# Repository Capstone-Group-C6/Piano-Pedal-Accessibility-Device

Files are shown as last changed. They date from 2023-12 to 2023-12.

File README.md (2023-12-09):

# Piano-Pedal-Accessibility-Device (PianoPAD)
Northeastern University 1st Place Capstone 2023 Open Source Repository for our PianoPAD system. Software designed by Roberto Chadwick, Lucas Laya Marina, and Luke Wisner. Hardware designed by Hanchen Liu, Josh Moffat, and Tristan Siu.

### General Overview
This project provides a way for people with a disability to use their piano pedals by tracking their head tilt and replicating it as pedal presses. The app is only for iOS devices, as we used Apple's Vision Library to get the necessary head tracking data. We wanted to make our work open-source so that anyone could make this device for themselves or anyone they know who would like the ability to use their piano pedals. Through the device that you plug into the piano port and the iOS application, we have created a system that can replicate pedal presses for one or three pedals. 

This idea began as a way to help Jonathan Goodwin for our engineering capstone project. Jonathan is a retired stunt performer and a current keynote speaker. Follow him at: https://www.instagram.com/jonathangoodwinofficial/?hl=en

Jonathan loves to play the piano, but he is unable to use the pedals because he was paralyzed from the waist down in an accident. We set out to create a device that would allow him to once again get full use from his piano. Through our initial meetings with Jonathan, we were able to discern the simplest, most intuitive way to make that possible: using the tilt of his head. The solutions that exist today all require the user to bite down on or blow into a device, but that would prevent Jonathan from being able to sing when he plays. The head tilt became the perfect solution because it fixed this issue while remaining intuitive to the user.

## Hardware
### Hardware Overview
One half of the PianoPAD system is the device that plugs into the back of the piano and replicates the pedal press signal. Anyone who wants to use this design in the future will need a chip capable of sending and recieving data over bluetooth (we used an ESP32 as a relatively inexpensive option so our schematics match that). In addition, they will need a way to power the device through micro-USB and connect the device to their piano pedal port using 1/4-inch jacks.

### Hardware Replication
The necessary KiCad files (schematic and PCB layout) have been added to allow anyone to replicate our board for their own personal use. The following images display the schematic design as well as the PCB layout of the components and traces involved in integrating all the parts of the board. 

<p align="center">
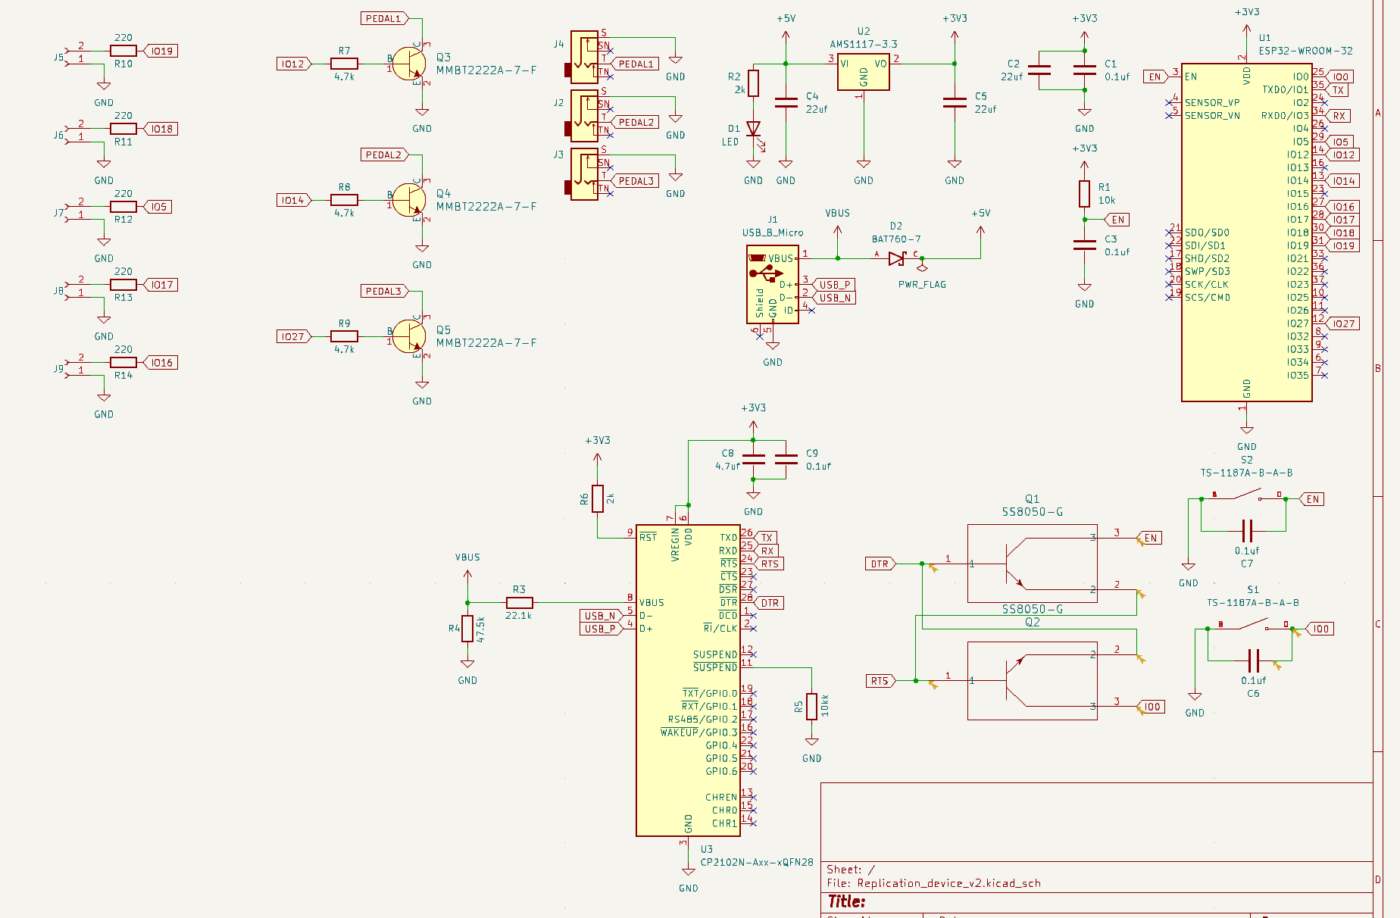
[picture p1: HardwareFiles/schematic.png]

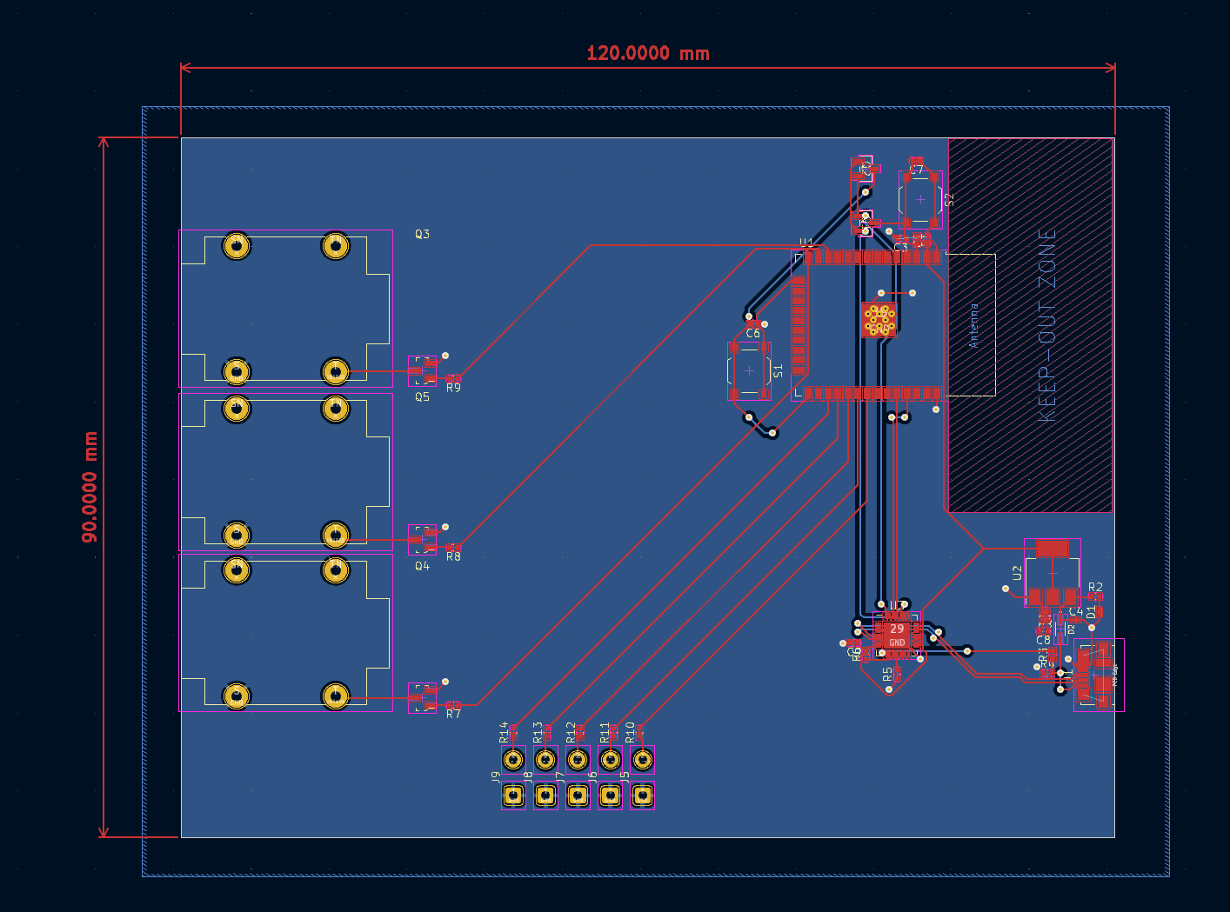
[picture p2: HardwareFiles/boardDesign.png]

</p>

In terms of the manufacturing and assembly process, orders can be made through various PCB manufacturers (we used JLCPCB.com) and provide them with our PCB/schematic files to make an order. Below is the part list with links to sites to purchase each component. (NOTE: You can also import the provided files into the KiCad project manager to view/make any changes to the project) In terms of assembly, be sure to solder on the components that are not already assembled onto the board from the manufacturer (i.e. 1/4" sockets...).

Parts List:
- 1/4" Socket: https://www.amazon.com/dp/B07MR2TT3Q?psc=1&smid=A34H4GNHCXU7L2&ref_=chk_typ_imgToDp
- LEDs: (https://www.amazon.com/eBoot-Pieces-Emitting-Diodes-Assorted/dp/B06XPV4CSH/ref=sr_1_8?crid=1UQGUEZ7QY5KU&keywords=leds&qid=1701737252&sprefix=leds%2Caps%2C88&sr=8-8&th=1)
- ESP32 Chip: [https://www.amazon.com/Development-Microcontroller-Integrated-Antenna-Amplifiers/dp/B09GK74F7N/ref=sr_1_1_sspa?crid=18ESI34J05HVB&keywords=esp32&qid=1701737319&sprefix=esp32%2Caps%2C82&sr=8-1-spons&sp_csd=d2lkZ2V0TmFtZT1zcF9hdGY&psc=1](https://www.amazon.com/Espressif-ESP32-S3-WROOM-1U-ESP32-S3-WROOM-1U-N8R8-Module/dp/B0B8NWF4F5/ref=sr_1_3?crid=3B4YTQOZYAYG1&keywords=esp32%2Bwroom%2B1u&qid=1701827727&sprefix=esp32%2Bwroom%2B1u%2Caps%2C95&sr=8-3&th=1)

### Three Pedal Proprietary Cable
Using three pedals with the device is a little more complicated because of how digital pianos are made. Any piano that can have a three-pedal attachment makes that connection through a proprietary cable instead of a standard 1/4-inch jack, so it was impossible to design a one-size-fits-all solution. Any users who want to use this functionality will have to create their own cable that ends in three 1/4-inch jacks to connect to the device. That way the other end of that cable can be the proper connection port that will work for their specific piano.

## Software
### Software Overview
The other half of the PianoPAD system is the iOS application that detects the head tilt and sends the signal over Bluetooth to the device. The app can be pushed to a TestFlight app for sharing with others, or the user can build directly to their phone through XCode. The app contains settings for selecting one or three pedals, changing the tilt direction, adjusting the threshold angle that triggers the tilt, toggling hold, and toggling inverse. The app has an additional page to give the user some directions on how to connect to the device through Bluetooth, and the best way to orient the phone when beginning a session. When the session view is started, it takes all of the saved data from settings, tracks the user's face, and begins sending data to the device to replicate the signal of the pedal press.

### Firmware Overview
The firmware that needs to be uploaded to the ESP32 chip also exists within this repository. It activates the necessary GPIO pins when it receives the packet from the application and it also contains the code necessary to establish the Bluetooth connection. The firmware then reads the sent byte to determine if any of the pedals are held down and which GPIO pins are activated if so.

### Bluetooth Connection
As stated above, the device establishes a connection when it is powered on, and the app with the corresponding UUID will be what it connects to. When the session is started in the app, it begins sending bytes where the last 3 bits trigger which pedals are currently being held down. 

### Head Tracking
The head tracking uses Apple's Vision Library to isolate features on the face and then return facial position data. This data includes the roll (tilting head side to side) and the pitch (tilting head up and down) in radians which allow us to determine the angle from the center position. The session tracks if the input radian threshold has been passed using this data, and that determines what data we send to the device to press the correct pedal. There is also a debounce implemented to prevent data flip-flopping when the user keeps their head right on the threshold. Additionally, the polling rate of the data is based on how new the iOS device is. The newer the device the smoother it will function, and we don't recommend running this system on anything older than an iPhone X.

### Navigating Settings
The settings page in the top right corner of the app allows the user to adjust what feels best to them when the session is running. There are two tabs for one pedal and three-pedal, which determines if the session will try to detect one or three directions. In the one pedal tab, the user has the ability to determine which way they want to tilt their head to pass the threshold, either left, right, both, or down. In addition, there are options to toggle inverse which presses the pedal unless the threshold is crossed, and toggle hold which keeps the state of the pedal when the threshold is crossed. There is a slider to adjust the angle with an example threshold bar beneath so that the user can test that angle and see what feels best for them. It was important to us to give the user as much freedom as possible to configure their sessions however they wanted to be natural for them.

<p align="center">
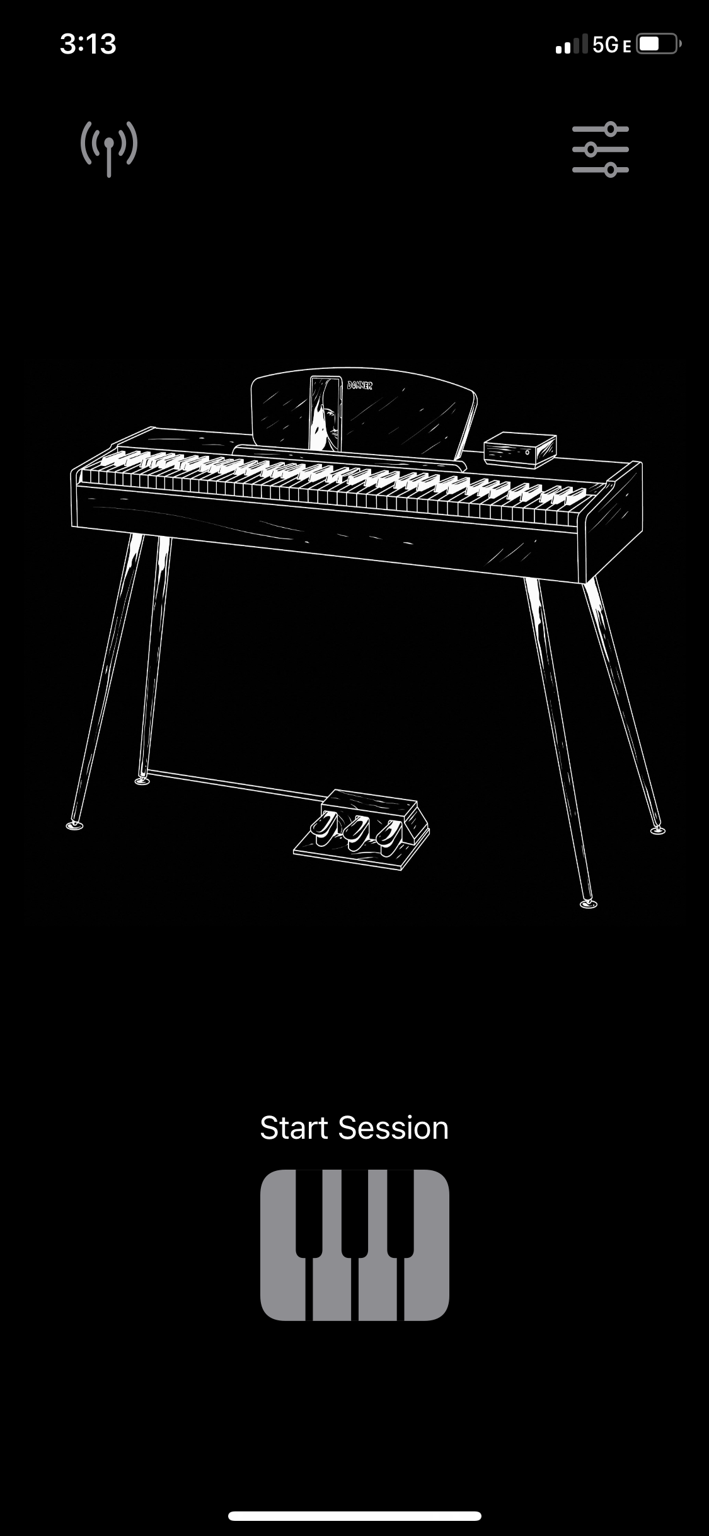
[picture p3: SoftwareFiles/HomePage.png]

</p>

<p align="center">
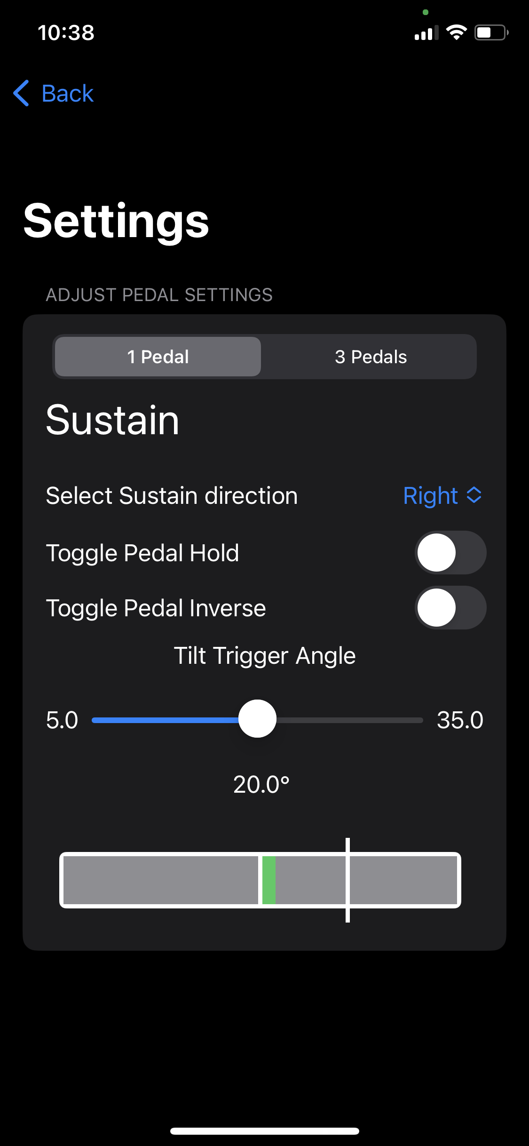
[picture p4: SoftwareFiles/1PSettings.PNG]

</p>

In the three-pedal system, the same options are available, except for the ability to hold and change directions for each pedal. The sustain and sostenuto pedals can have their directions switched to change which one is left and right, but the soft pedal is locked as tilting downward. This is because when playing the piano, the soft pedal is the only other pedal that can be used in tandem with the other two. Given that you can't tilt your head both left and right at the same time, but you can tilt down and right, we decided to keep the soft pedal as only down. Each of these three pedals has the ability to be active or inactive, so if a song doesn't require a specific pedal, you can turn it off to avoid triggering it by accident. These pedals also all have angle adjustment sliders and threshold bars to give the user a visual of what angles would work best for them.

<p align="center">
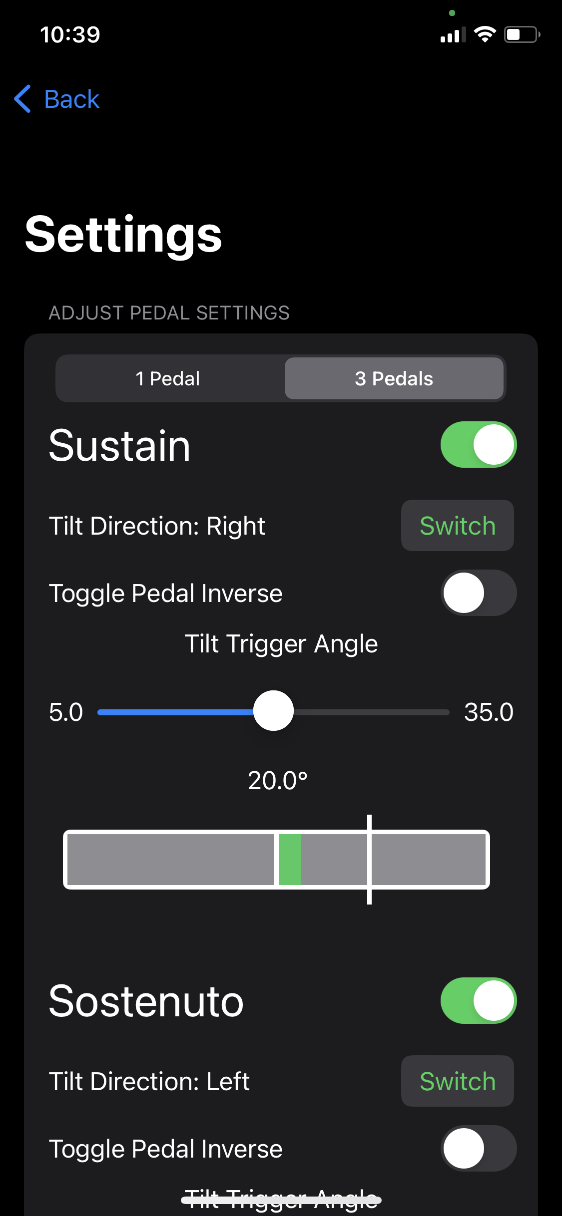
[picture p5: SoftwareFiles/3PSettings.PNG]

</p>

When the session begins, the saved settings variables are processed between specified cases that run the head-tracking logic. There is a case to handle every possible combination of toggles and angle values in both the one and three-pedal systems. The user can then see these settings in action through the indicator bars in the session view. There are the same threshold bars to show how far the user's head is tilting, and at the bottom, there are indicator bars to show which pedals are activated and sending a signal to the device.

<p align="center">
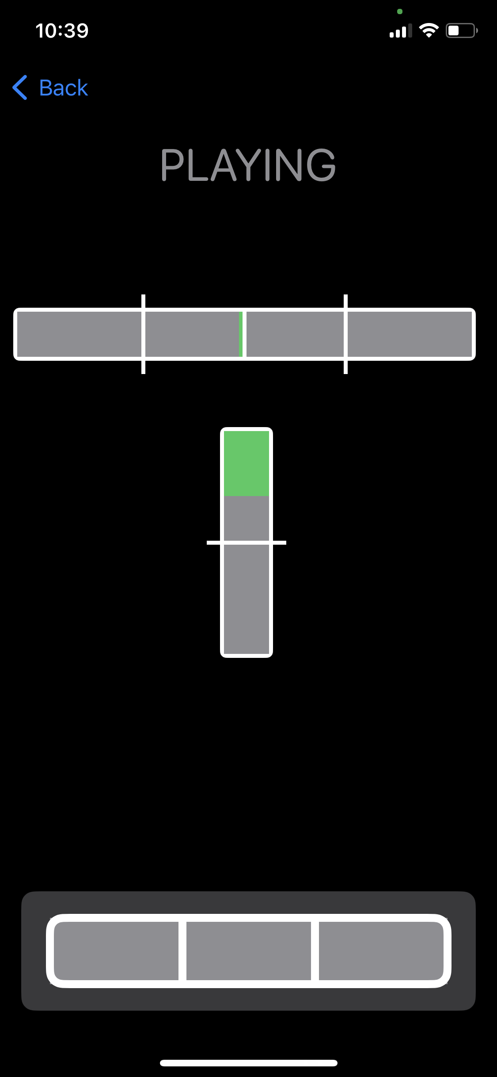
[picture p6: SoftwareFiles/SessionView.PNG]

</p>

### Software Replication
To replicate the software, the user will need to flash the firmware onto the chip they have started using. From there, the app can be run through XCode with no additional changes and be built into an iPhone for testing. Additionally, if the user wants to share the app with others, they can get an Apple Developer License and push the app to TestFlight where it can be downloaded on any iOS device. The backend functions that deal with Bluetooth connection and face tracking can be found in the model, and all of the frontend app pages can be found in the view. 

## Additional Implementations 
Another reason that we wanted to make this code publicly available is that it has so many other applications to help anyone with disabilities. We designed the app with a piano in mind, but the code can be repurposed to work with another instrument such as a guitar or drumset. Further beyond this, the head tracking functions could be expanded upon to communicate with non-instrument devices like a wheelchair. We hope that this code can help any who uses it!

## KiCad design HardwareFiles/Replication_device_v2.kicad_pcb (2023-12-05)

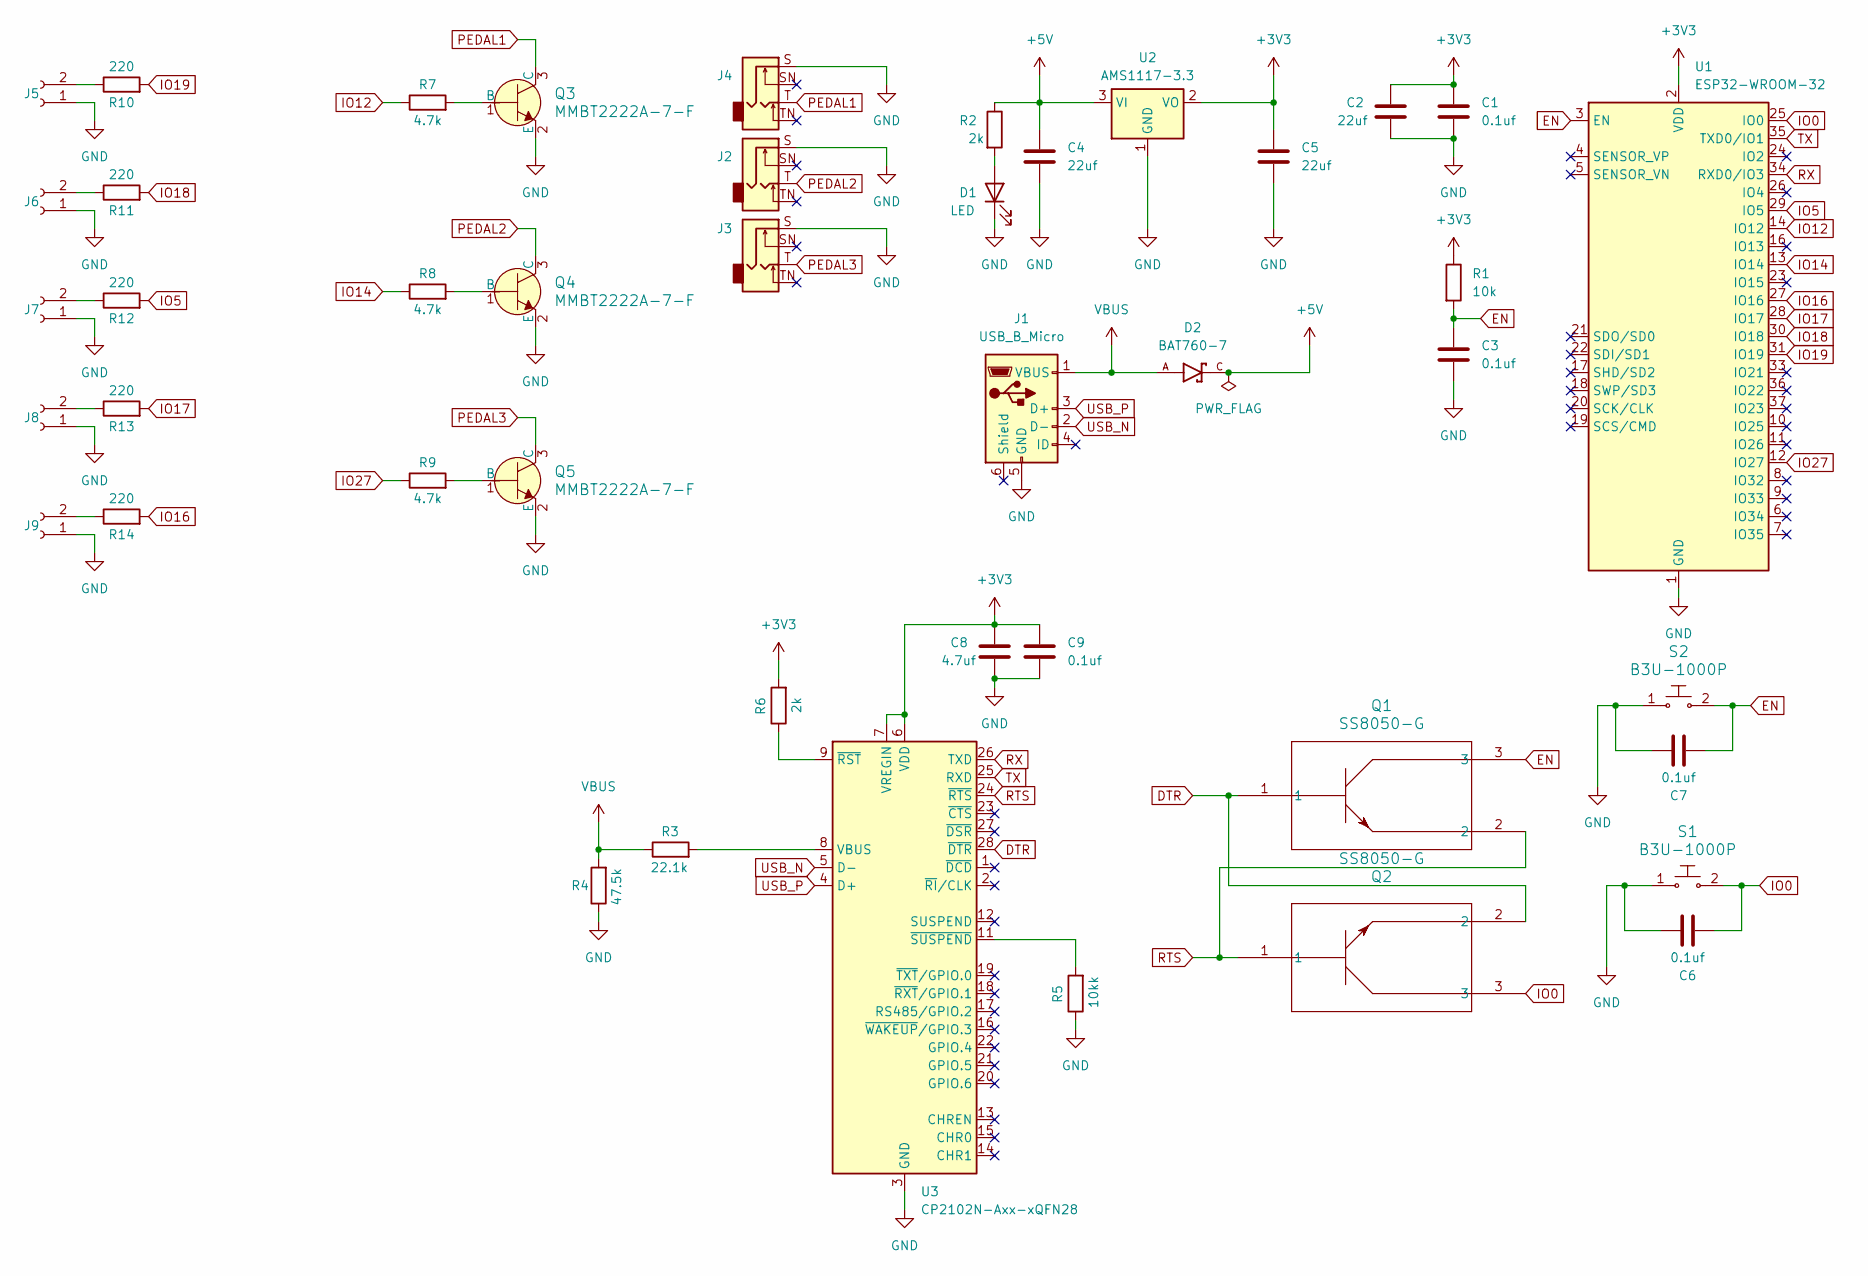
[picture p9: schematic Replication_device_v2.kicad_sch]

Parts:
C1, C3, C6, C7, C9: 0.1uf; C_0402_1005Metric
C2, C4, C5: 22uf; C_0603_1608Metric
C8: 4.7uf; C_0402_1005Metric
D1: LED; LED_0603_1608Metric
D2: BAT760-7; SOD2513X120N; PARTREV 9-2
J1: USB_B_Micro; USB_Micro-B_Molex_47346-0001
J2, J3, J4: AudioJack2_Switch; Jack_6.35mm_Neutrik_NMJ4HCD2_Horizontal
J5, J6, J7, J8, J9: Conn_01x02_Socket; SolderWire-0.5sqmm_1x02_P4.6mm_D0.9mm_OD2.1mm
Q1, Q2: SS8050-G; TRAN_SS8050-G_CIP
Q3, Q4, Q5: MMBT2222A-7-F; SOT-23-3; MPN MMBT2222A-7-F; Digi-Key_PN MMBT2222A-FDICT-ND
R1: 10k; R_0402_1005Metric
R2, R6: 2k; R_0402_1005Metric
R3: 22.1k; R_0402_1005Metric
R4: 47.5k; R_0402_1005Metric
R5: 10kk; R_0402_1005Metric
R7, R8, R9: 4.7k; R_0402_1005Metric
R10, R11, R12, R13, R14: 220; R_0402_1005Metric
S1, S2: B3U-1000P; SW_Push_1P1T_XKB_TS-1187A; MPN B3U-1000P; Digi-Key_PN SW1020CT-ND
U1: ESP32-WROOM-32
U2: AMS1117-3.3; SOT-223-3_TabPin2
U3: CP2102N-Axx-xQFN28; QFN-28-1EP_5x5mm_P0.5mm_EP3.35x3.35mm

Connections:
+3V3: C1.1, C2.1, C5.1, C8.1, C9.1, R1.1, R6.2, U1.2 (VDD), U2.2 (VO), U3.6 (VDD), U3.7 (VREGIN)
+5V: C4.1, D2.C, R2.1, U2.3 (VI)
DTR: Q1.1, Q2.2, U3.28 (~DTR)
EN: C3.1, C7.2, Q1.3, R1.2, S2.2, U1.3 (EN)
GND: C1.2, C2.2, C3.2, C4.2, C5.2, C6.1, C7.1, C8.2, C9.2, D1.1 (K), J1.5 (GND), J2.S, J3.S, J4.S, J5.1, J6.1, J7.1, J8.1, J9.1, Q3.2 (E), Q4.2 (E), Q5.2 (E), R4.1, R5.1, S1.1, S2.1, U1.1 (GND), U1.15 (GND), U1.38 (GND), U1.39 (GND), U2.1 (GND), U3.3 (GND), U3.29 (GND)
IO0: C6.2, Q2.3, S1.2, U1.25 (IO0)
IO5: R12.2, U1.29 (IO5)
IO12: R7.1, U1.14 (IO12)
IO14: R8.1, U1.13 (IO14)
IO16: R14.2, U1.27 (IO16)
IO17: R13.2, U1.28 (IO17)
IO18: R11.2, U1.30 (IO18)
IO19: R10.2, U1.31 (IO19)
IO27: R9.1, U1.12 (IO27)
unnamed: D1.2 (A), R2.2
unnamed: J5.2, R10.1
unnamed: J6.2, R11.1
unnamed: J7.2, R12.1
unnamed: J8.2, R13.1
unnamed: J9.2, R14.1
unnamed: Q3.1 (B), R7.2
unnamed: Q4.1 (B), R8.2
unnamed: Q5.1 (B), R9.2
unnamed: R3.2, U3.8 (VBUS)
unnamed: R6.1, U3.9 (~RST)
unnamed: R5.2, U3.11 (~SUSPEND)
PEDAL1: J4.T, Q3.3 (C)
PEDAL2: J2.T, Q4.3 (C)
PEDAL3: J3.T, Q5.3 (C)
RTS: Q1.2, Q2.1, U3.24 (~RTS)
RX: U1.34 (RXD0/IO3), U3.26 (TXD)
TX: U1.35 (TXD0/IO1), U3.25 (RXD)
USB_N: J1.2 (D-), U3.5 (D-)
USB_P: J1.3 (D+), U3.4 (D+)
VBUS: D2.A, J1.1 (VBUS), R3.1, R4.2

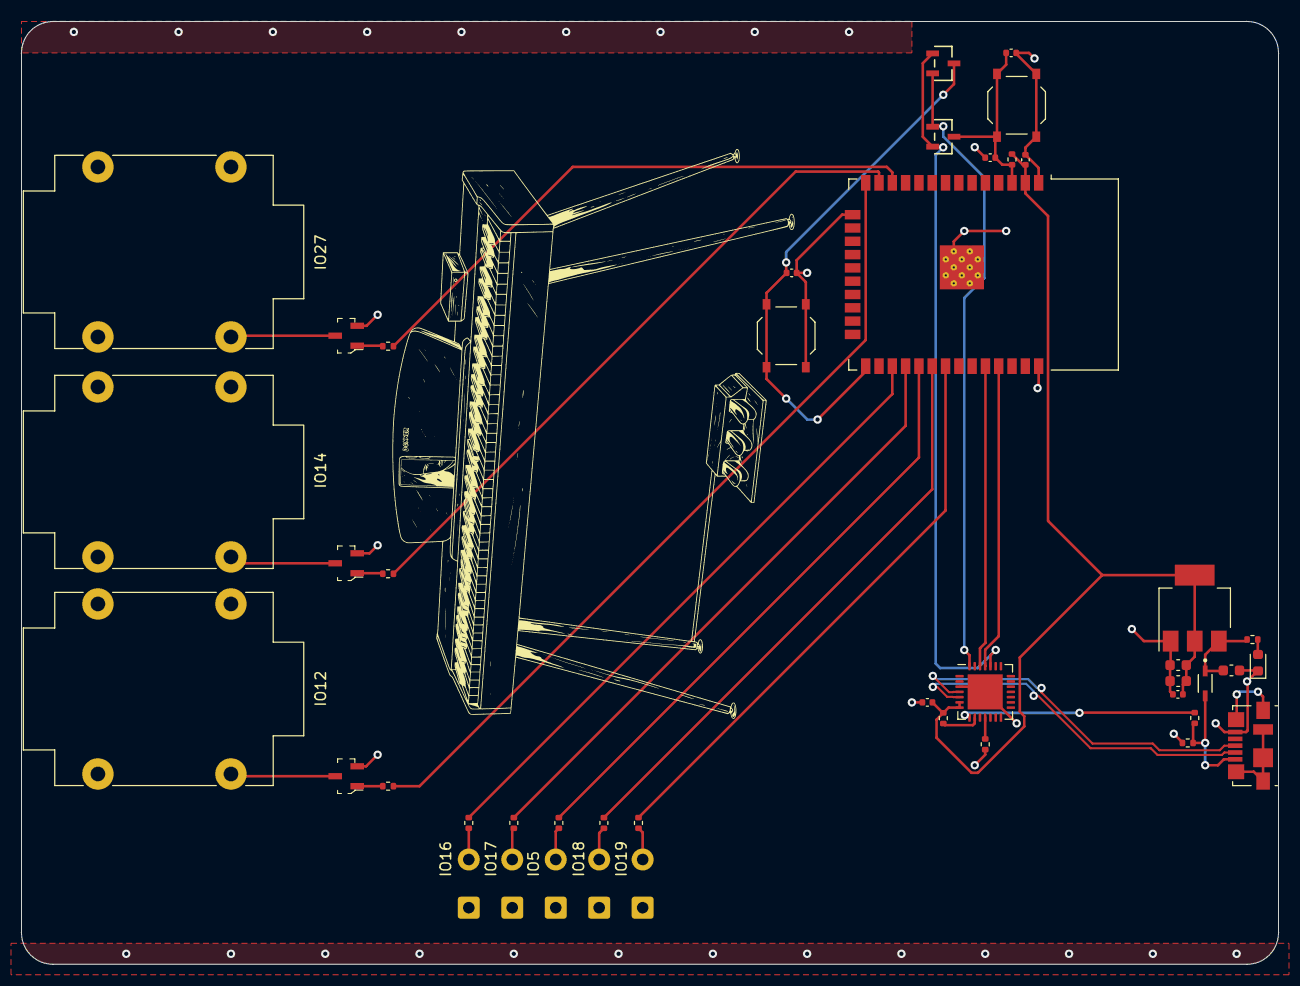
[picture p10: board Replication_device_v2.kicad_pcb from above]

Board: 2 copper layers, 120.0 x 90.0 mm, 44 parts (0 on the bottom side), 35 nets.

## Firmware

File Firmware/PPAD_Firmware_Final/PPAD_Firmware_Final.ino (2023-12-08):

/*

  Piano Pedal Replication Device Firmware V3

*/

#include <ArduinoBLE.h>

#define NUMPEDALS 3

static int MPIO0 = 36; //labelled on board as 16 
static int MPIO1 = 37; //labelled on board as 17
static int MPIO2 = 38; //labelled on board as 5
static int MPIO3 = 39; //labelled on board as 18
static int MPIO4 = 40; //labelled on board as 19

static int pedal0 = 8; //labelled on board as 14
static int pedal1 = 19; //labelled on board as 27
static int pedal2 = 20; //labelled on board as 12

void setPedalAndLED(int pedalNum, uint8_t state) {
  switch (pedalNum) {
    case 0:
      digitalWrite(pedal0, state);
      digitalWrite(MPIO0, state);
      break;
    case 1:
      digitalWrite(pedal1, state);
      digitalWrite(MPIO1, state);
      break;
    case 2:
      digitalWrite(pedal2, state);
      digitalWrite(MPIO2, state);
      break;
  }
}

void resetPedalsAndLEDs() {
  for (int i = 0; i < NUMPEDALS; i++) {
    setPedalAndLED(i, LOW);
  }
}

void setup() {
  Serial.begin(115200);
  while (!Serial);
  Serial.println("PPAD - Replication Device");

  // configure the multi-purpose IOs as outputs
  pinMode(MPIO0, OUTPUT);
  pinMode(MPIO1, OUTPUT);
  pinMode(MPIO2, OUTPUT);
  pinMode(MPIO3, OUTPUT);
  pinMode(MPIO4, OUTPUT);

  // configure the pedals as outputs
  pinMode(pedal0, OUTPUT);
  pinMode(pedal1, OUTPUT);
  pinMode(pedal2, OUTPUT);

  // initialize the Bluetooth® Low Energy hardware
  BLE.begin();
  Serial.println("Starting BLE...");
  

  // start scanning for peripherals
  BLE.scanForUuid("ac6c445f-58e8-4c22-a2fc-191199030025");
}

void loop() {
  // check if a peripheral has been discovered
  BLEDevice peripheral = BLE.available();

  if (peripheral) {
    Serial.print("Found ");
    Serial.print(peripheral.address());
    Serial.print(" '");
    Serial.print(peripheral.localName());
    Serial.print("' ");
    Serial.print(peripheral.advertisedServiceUuid());
    Serial.println();

    // stop scanning
    BLE.stopScan();

    controlLed(peripheral);

    // peripheral disconnected, start scanning again
    BLE.scanForUuid("ac6c445f-58e8-4c22-a2fc-191199030025");
  }
}

void controlLed(BLEDevice peripheral) {
  // connect to the peripheral
  Serial.println("Connecting ...");

  if (peripheral.connect()) {
    Serial.println("Connected");
    digitalWrite(MPIO3, HIGH);
  } else {
    Serial.println("Failed to connect!");
    return;
  }

  // discover peripheral attributes
  Serial.println("Discovering attributes ...");
  if (peripheral.discoverAttributes()) {
    Serial.println("Attributes discovered");
  } else {
    Serial.println("Attribute discovery failed!");
    peripheral.disconnect();
    return;
  }

  BLECharacteristic pianoCharacteristic = peripheral.characteristic("3d04e7ac-13f2-4713-ae66-d67b80a4c5a3");

  if (!pianoCharacteristic) {
    Serial.println("Peripheral does not have the characteristic!");
    peripheral.disconnect();
    return;
  }

  while (peripheral.connected()) {
    // while the peripheral is connected

    // Subscribe to the ppad characteristic
    pianoCharacteristic.subscribe();
    
    while(peripheral.connected()) {
      if(pianoCharacteristic.valueUpdated()){
        byte value = 0;
        char* valPointer = (char*) &value;
        pianoCharacteristic.readValue(value);
        
        // If value is in character format, convert to byte
        if (value >= 8)
          value = (byte) atoi((char*) valPointer);

        Serial.println(value, BIN); // show the binary value 

        if (value & 0b00000100) {
          setPedalAndLED(0, HIGH);
        } else {
          setPedalAndLED(0, LOW);
        }

        if (value & 0b00000010) {
          setPedalAndLED(1, HIGH);
        } else {
          setPedalAndLED(1, LOW);
        }

        if (value & 0b00000001) {
          setPedalAndLED(2, HIGH);
        } else {
          setPedalAndLED(2, LOW);
        }
      }
    }
  }

  digitalWrite(MPIO3, LOW);
  resetPedalsAndLEDs();
  Serial.println("Peripheral disconnected");
}

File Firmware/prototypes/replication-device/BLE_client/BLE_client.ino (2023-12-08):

/**
 * A BLE client example that is rich in capabilities.
 * There is a lot new capabilities implemented.
 * author unknown
 * updated by chegewara
 */

#include "BLEDevice.h"
//#include "BLEScan.h"

// The remote service we wish to connect to.
static BLEUUID serviceUUID("4fafc201-1fb5-459e-8fcc-c5c9c331914b");
// The characteristic of the remote service we are interested in.
static BLEUUID    charUUID("beb5483e-36e1-4688-b7f5-ea07361b26a8");

static boolean doConnect = false;
static boolean connected = false;
static boolean doScan = false;
static BLERemoteCharacteristic* pRemoteCharacteristic;
static BLEAdvertisedDevice* myDevice;


static void notifyCallback(
  BLERemoteCharacteristic* pBLERemoteCharacteristic,
  uint8_t* pData,
  size_t length,
  bool isNotify) {
    /*
    Serial.println(*pData);
    if (pData[0] & 0b00000001) {
      //sustain on
      digitalWrite(5, HIGH);
      Serial.println("Sustain pedal: ON");
    } else {
      digitalWrite(5, LOW);
      Serial.println("Sustain pedal: OFF");
    }

    if (pData[0] & 0b00000010) {
      //Middle on
      digitalWrite(6, HIGH);
      Serial.println("Middle pedal: ON");
    } else {
      digitalWrite(6, LOW);
      Serial.println("Middle pedal: OFF");
    }
    
    if (pData[0] & 0b00000100) {
      //sustain on
      digitalWrite(7, HIGH);
      Serial.println("Sustain pedal: ON");
    } else {
      digitalWrite(7, LOW);
      Serial.println("Sustain pedal: OFF");
    }
    */
}

class MyClientCallback : public BLEClientCallbacks {
  void onConnect(BLEClient* pclient) {
  }

  void onDisconnect(BLEClient* pclient) {
    connected = false;
    Serial.println("onDisconnect");
  }
};

bool connectToServer() {
    Serial.print("Forming a connection to ");
    Serial.println(myDevice->getAddress().toString().c_str());
    
    BLEClient*  pClient  = BLEDevice::createClient();
    Serial.println(" - Created client");

    pClient->setClientCallbacks(new MyClientCallback());

    // Connect to the remove BLE Server.
    pClient->connect(myDevice);  // if you pass BLEAdvertisedDevice instead of address, it will be recognized type of peer device address (public or private)
    Serial.println(" - Connected to server");

    // Obtain a reference to the service we are after in the remote BLE server.
    BLERemoteService* pRemoteService = pClient->getService(serviceUUID);
    if (pRemoteService == nullptr) {
      Serial.print("Failed to find our service UUID: ");
      Serial.println(serviceUUID.toString().c_str());
      pClient->disconnect();
      return false;
    }
    Serial.println(" - Found our service");


    // Obtain a reference to the characteristic in the service of the remote BLE server.
    pRemoteCharacteristic = pRemoteService->getCharacteristic(charUUID);
    if (pRemoteCharacteristic == nullptr) {
      Serial.print("Failed to find our characteristic UUID: ");
      Serial.println(charUUID.toString().c_str());
      pClient->disconnect();
      return false;
    }
    Serial.println(" - Found our characteristic");
    /*
    // Read the value of the characteristic.
    if(pRemoteCharacteristic->canRead()) {
      std::string value = pRemoteCharacteristic->readValue();
      Serial.print("The characteristic value was: ");
      Serial.println(value.c_str());
    }
    */
    if(pRemoteCharacteristic->canNotify())
      pRemoteCharacteristic->registerForNotify(notifyCallback);

    connected = true;
}
/**
 * Scan for BLE servers and find the first one that advertises the service we are looking for.
 */
class MyAdvertisedDeviceCallbacks: public BLEAdvertisedDeviceCallbacks {
 /**
   * Called for each advertising BLE server.
   */
  void onResult(BLEAdvertisedDevice advertisedDevice) {
    Serial.print("BLE Advertised Device found: ");
    Serial.println(advertisedDevice.toString().c_str());

    // We have found a device, let us now see if it contains the service we are looking for.
    if (advertisedDevice.haveServiceUUID() && advertisedDevice.isAdvertisingService(serviceUUID)) {

      BLEDevice::getScan()->stop();
      myDevice = new BLEAdvertisedDevice(advertisedDevice);
      doConnect = true;
      doScan = true;

    } // Found our server
  } // onResult
}; // MyAdvertisedDeviceCallbacks


void setup() {
  Serial.begin(115200);
  Serial.println("Starting Arduino BLE Client application...");
  BLEDevice::init("");

  // Retrieve a Scanner and set the callback we want to use to be informed when we
  // have detected a new device.  Specify that we want active scanning and start the
  // scan to run for 5 seconds.
  BLEScan* pBLEScan = BLEDevice::getScan();
  pBLEScan->setAdvertisedDeviceCallbacks(new MyAdvertisedDeviceCallbacks());
  pBLEScan->setInterval(1349);
  pBLEScan->setWindow(449);
  pBLEScan->setActiveScan(true);
  pBLEScan->start(5, false);
  pinMode(5, OUTPUT);
  pinMode(6, OUTPUT);
  pinMode(7, OUTPUT);
  pinMode(2, OUTPUT);
} // End of setup.


// This is the Arduino main loop function.
void loop() {

  // If the flag "doConnect" is true then we have scanned for and found the desired
  // BLE Server with which we wish to connect.  Now we connect to it.  Once we are 
  // connected we set the connected flag to be true.
  if (doConnect == true) {
    if (connectToServer()) {
      Serial.println("We are now connected to the BLE Server.");
      digitalWrite(2, HIGH);
    } else {
      Serial.println("We have failed to connect to the server; there is nothin more we will do.");
    }
    doConnect = false;
  }

  // If we are connected to a peer BLE Server, update the characteristic each time we are reached
  // with the current time since boot.
  if (connected) {
    String newValue = "Time since boot: " + String(millis()/1000);
    Serial.println("Setting new characteristic value to \"" + newValue + "\"");
    
    // Set the characteristic's value to be the array of bytes that is actually a string.
    pRemoteCharacteristic->writeValue(newValue.c_str(), newValue.length());
  }else if(doScan){
    BLEDevice::getScan()->start(0);  // this is just eample to start scan after disconnect, most likely there is better way to do it in arduino
  }
  
  delay(1000); // Delay a second between loops.
} // End of loop

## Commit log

2023-12-05 Add files via upload
    Added schematic files for recreating the PPAD device
    [Replication_device_v2.kicad_pcb, Replication_device_v2.kicad_sch]
2023-12-05 Added all app files, organized hardware files, and attached Piano logos
    [Replication_device_v2.kicad_pcb, Replication_device_v2.kicad_sch]
2023-12-06 Update README.md
    Updated ESP32 chip link, some small text errors fixed
